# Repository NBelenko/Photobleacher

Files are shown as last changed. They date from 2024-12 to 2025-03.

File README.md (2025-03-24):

# Photobleacher

Photobleacher is an open-source photobleaching device designed to bleach autofluorescence and pigments in biological materials. For more details about the project, please refer to our [publication](https://doi.org/10.1101/2025.02.24.639965).

## About This Repository

This repository contains the following materials.

1. CAD file of the chassis (Enclosure CAD)
2. PCB board design (PCB)
3. Sample stage design (Sample Stage)
4. List of components (Main BOM.xlsx)
5. Wiring diagram (PB Block & Wiring Diagram.pdf)
6. Assembly instructions (PB_Assembly Instructions.pdf)

## Citation

> Murakami et al. Open-source Photobleacher for Fluorescent Imaging of Large Pigment-Rich Tissues. bioRxiv (2025) https://doi.org/10.1101/2025.02.24.639965 

## License

We provide this open source software without any warranty under the [MIT license](https://opensource.org/licenses/MIT).

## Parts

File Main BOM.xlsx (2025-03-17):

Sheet: Enclosure - Digikey
Description | MFGR P/N | Digikey P/N | Qty | Notes
AC/DC CONVERTER 24V 200W | CUS200M-24 | 285-CUS200M-24-ND | 1 | Main PSU
FAN AXIAL 92X20MM 24VDC WIRE | AFB0924HD | 603-1063-ND | 4 | Main Stage Fan
FAN AXIAL 50X20MM 24VDC WIRE | AFB0524VHD | 603-1283-ND | 2 | PSU Fan
PWR ENT MOD RCPT IEC320-C14 PNL | KM01.1205.11 | 486-2280-ND | 1 | PEM (IEC320-C14)
FUSE DRWR FOR PWR MOD F'GRIP 1PL | 4301.1405 | 486-1956-ND | 1 | Fuse drawer for PEM
RELAY GEN PURPOSE DPDT 10A 120V | LY2F-AC110/120 | Z6232-ND | 1 | Power output Relay
FUSE GLASS 2.5A 125VAC 5X20MM | 7010.345 | 486-1837-ND | 1 | Fuse for PEM
CONN RCPT HSG 5POS 3.96MM | VHR-5N | 455-1186-ND | 1 | Input Power connector (AC)
CONN RCPT HSG 6POS 3.96MM | VHR-6N | 455-1187-ND | 1 | Output Power Connector (DC)
CONN SOCKET 18-22AWG CRIMP TIN | SVH-21T-P1.1 | 455-1133-1-ND | 3 | crimp contact for AC input
CONN SOCKET 16-20AWG CRIMP TIN | SVH-41T-P1.1 | 455-1319-1-ND | 6 | crimp contact for DC output
SWITCH ROCKER SPST 16A 125V | KRE2ALA2RBB | CH933-ND | 1 | Front Panel Rocker Switch
CONN QC RCPT 18-22AWG 0.187 | 190030011 | WM18238-ND | Bulk | red QC Female
CONN QC RCPT 14-16AWG 0.187 | 190030056 | WM11242-ND | Bulk | blue QC Female
CONN QC RCPT 18-22AWG 0.187 | 190070010 | WM14190CT-ND | Bulk | red QC Female (flag)
CONN QC RCPT 14-16AWG 0.187 | 190070035 | WM13547-ND | Bulk | blue QC Female (flag)
FILTR ASSB FAN GUARD 92MM 45PPI | 09362-F/45 | CR329-ND | 4 | inlet/Outlet fan cover
FAN GUARD 50MM METAL | 08248 | CR379-ND | 4 | PSU Fan Covers
CONN SPADE TERM 18-22AWG #10 RED | 191420007 | WM13785-ND | Bulk | Spade Power Connector (18-22AWG)
CONN SPADE TERM 14-16AWG #10 BLU | 191310014 | WM13770-ND | Bulk | Spade Power Connector (14-16AWG)
SENSOR REED SW SPST-NO W LEADS | 59150-020 | 59150-020-ND | 1 | Reed Switch for Door
MAGNET 0.375"D X 0.100"THICK CYL | 8008 | 469-1010-ND | 1 | Magnet for Door
HOOK-UP STRND 18AWG BLACK 100' | 891819 BK005 | 891819BK005-ND | 1 | Bulk 18AWG Wire - Black
HOOK-UP STRND 18AWG RED 100' | 891819 RD005 | 891819RD005-ND | 1 | Bulk 18AWG Wire - Red
CONN RING CIRC 14-16AWG #8 CRIMP | 190540110 | WM13634-ND | Bulk | Ring Connector For Terminal Block Bus
Blue Sea Systems DualBus 100A Comon BusBars | 2702 | N/A | 1 | Amazon ASIN: B000277JB4 (Not on Digikey)
SEE PCB Folder For PCB Part BOM

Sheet: Enclosure - McMaster-Carr
Description | McMaster P/N | Qty | Notes
Silicone Sealant Dow Corning 732, 10.1 FL. oz. Cartridge, White | 7587A31 | 1 | Sealant for Spillproofing
Chemical-Resistant Santoprene Sealing Washer (QTY 50) | 94733A411 | 1 | Washers for Stage Spillproofing
Borosilicate Glass Sheet 12" x 8" x 1/4" | 8476K84 | 1 | Glass Sheet for Stage
18-8 Stainless Steel M3 Hex Nuts (QTY 100) | 91828A211 | 1
18-8 Stainless Steel Socket Head Screw M3 x 0.5 mm Thread, 10 mm Long (QTY 100) | 91292A113 | 1 | General purpose mounting screws for LED boards
18-8 Stainless Steel Cup-Point Set Screw M3 x 0.5 mm Thread, 10 mm Long (QTY 50) | 92015A106 | 1 | For Mounting Glass Stage
Female Threaded Hex Standoff 18-8 Stainless Steel, 4.5mm Hex, 10mm Long, M3 x 0.5mm Thread | 94868A006 | 8 | For Mounting Glass Stage
316 Stainless Steel Button Head Hex Drive Screw Super-Corrosion-Resistant, 6-32 Thread Size, 1-1/4" Long (QTY 50) | 98164A444 | 1 | Fan Mounting Hardware
316 Stainless Steel Button Head Hex Drive Screw Super-Corrosion-Resistant, 6-32 Thread Size, 1-1/2" Long (QTY 50) | 98164A445 | 1 | Fan Mounting Hardware
18-8 Stainless Steel Narrow Hex Nut 6-32 Thread Size (QTY 100) | 90730A007 | 1 | Fan Mounting Hardware
High-Temperature Foam Mounting Tape 3M VHB 4611, 1/2" Wide, 15 Feet Long | 7201A21 | 1 | Foam VHB tape for Mounting Parts inside enclosure

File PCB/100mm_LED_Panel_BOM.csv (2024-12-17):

Source: | C:\Users\Griffin\Dropbox (Dropbox @RU)\Precision Instrumentation Technologies\Rockefeller Labs\Heintz Lab (PIT)\Tatz\HEI-2300 Photobleaching Device for Brain Imaging\100mm_LED_Panel\100mm_LED_Panel.kicad_sch
Date: | 1/24/2024 17:04
Tool: | Eeschema (6.0.7)
Generator: | C:\Program Files\KiCad\6.0\bin\scripting\plugins/bom_csv_grouped_by_value.py
Component Count: | 97
Components
Item | Qty | Reference(s) | Value | LibPart | Footprint | Datasheet | DigiKey P/N | Manufacturer | Part Num
1 | 8 | C1-C8 | 0.1u | Device:C_Polarized | Capacitor_Tantalum_SMD:CP_EIA-3216-18_Kemet-A | ~ | 399-3676-1-ND | KEMET | T491A104K035AT
2 | 64 | D1-D64 | LED | Device:LED | Library:LED_Luminus_MP-3030-1100_3.0x3.0mm_Thermal-Vias | ~ | 1214-MP-3030-120H-30-80CT-ND | Luminus Devices Inc. | MP-3030-120H-30-80
3 | 1 | F1 | Polyfuse | Device:Polyfuse | Library:Fuse_2018_5045Metric_Pad_HandSolder | ~ | DECASMDC050F/60-2CT-ND | Littelfuse Inc. | DECASMDC050F/60-2
4 | 4 | J1-J4 | HERM-4-PIN | 100mm_LED_Panel:HERM-4-PIN | Library:TE 2213611-2 4 Position Mini-HERM |  | A124894CT-ND | TE Connectivity AMP Connectors | 2213611-2
5 | 4 | J5-J12 | N/A | Connector_Generic:Conn_01x01 | Library:Faston .25 Tab | ~ | A29938CT-ND | TE Connectivity AMP Connectors | 63824-1
6 | 8 | R1-R8 | 11R | Device:R | Resistor_SMD:R_1206_3216Metric_Pad1.30x1.75mm_HandSolder | ~ | 541-10568-1-ND | Vishay Dale | RCS120611R0FKEA
Collated Components:

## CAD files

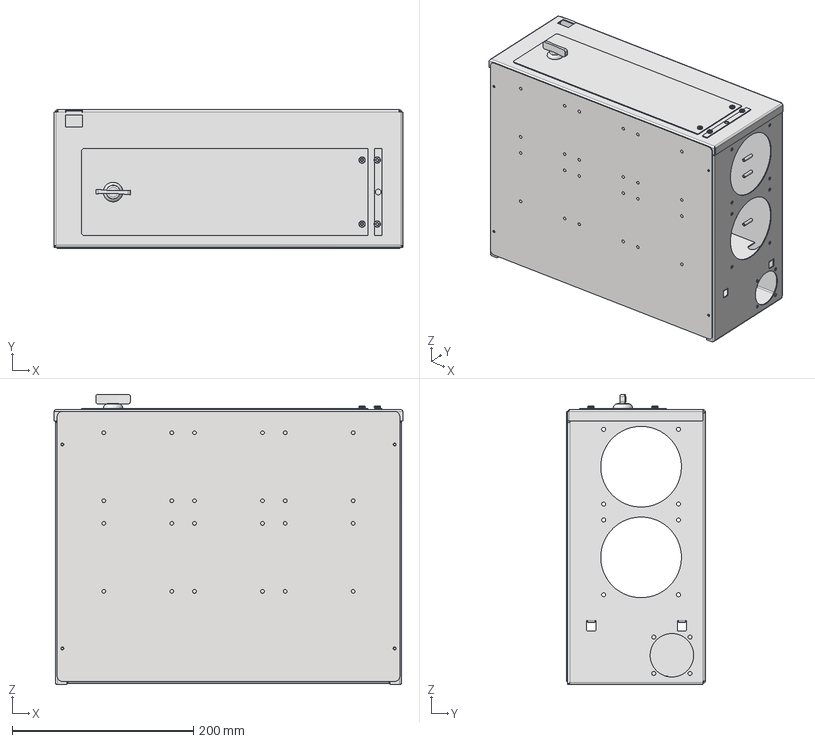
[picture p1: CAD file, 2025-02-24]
Enclosure CAD/RU_Photobleacher_Main_REV_A.stp
385.0 x 153.2 x 320.4 mm
Photobleacher Enclosure Base
Photobleacher Top Cover
Door
Spacer
Bulkhead Plate
1820A21_1820A210-3_8
CLS-M3-1_CLS-M3-1 x 6
BSO-M3-8ZI_BSO-M3-8ZI x 4
BSO-M3-18ZI_BSO-M3-18ZI x 24
BSO-M3-14ZI_BSO-M3-14ZI x 24
S-632-0ZI_S-632-0ZI x 4

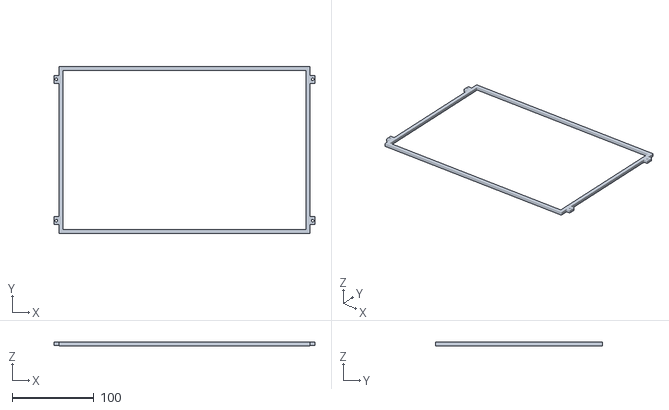
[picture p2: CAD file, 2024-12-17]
Sample Stage/Spill_Tray_bezel.stl
319.6 x 204.6 x 4.50

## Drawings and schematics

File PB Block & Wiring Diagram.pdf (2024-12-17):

## AC Power Input

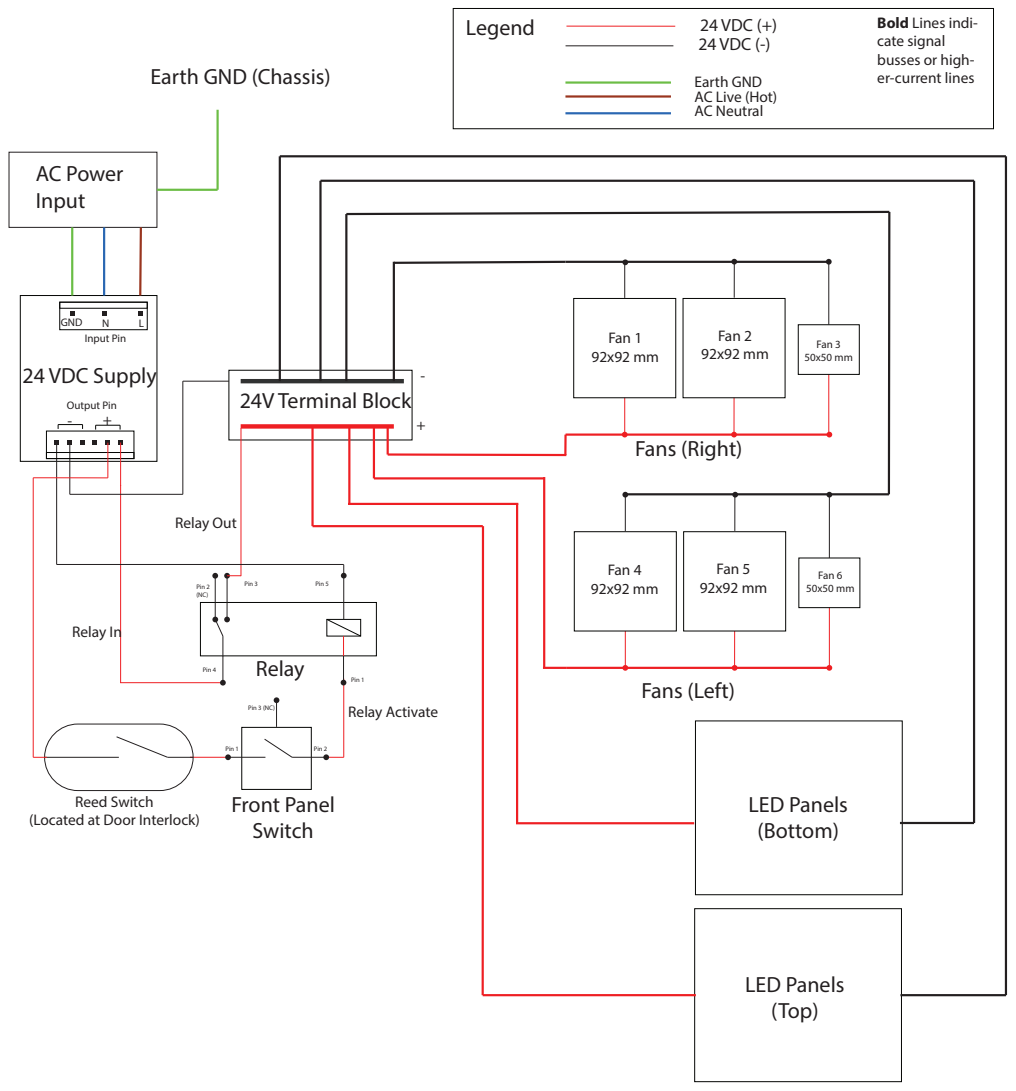
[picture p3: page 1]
24 VDC Supply; Legend; Front Panel Switch; Relay; Relay In; Relay Activate; 24V Terminal Block; Relay Out; Fans (Left); Fans (Right); Fan 4 92x92 mm; LED Panels (Bottom); LED Panels (Top); Pin 1; Pin 2; Pin 3 (NC); Pin 5; Pin 4; Pin 2 (NC); Pin 3; 24 VDC (+) 24 VDC (-); GND; Input Pin; Output Pin; Fan 5 92x92 mm; Fan 6 50x50 mm; Fan 1 92x92 mm; Fan 2 92x92 mm; Fan 3 50x50 mm

Bold Lines indi-
cate signal
busses or high-
er-current lines

Earth GND (Chassis)

Earth GND
AC Live (Hot)
AC Neutral

Reed Switch
(Located at Door Interlock)

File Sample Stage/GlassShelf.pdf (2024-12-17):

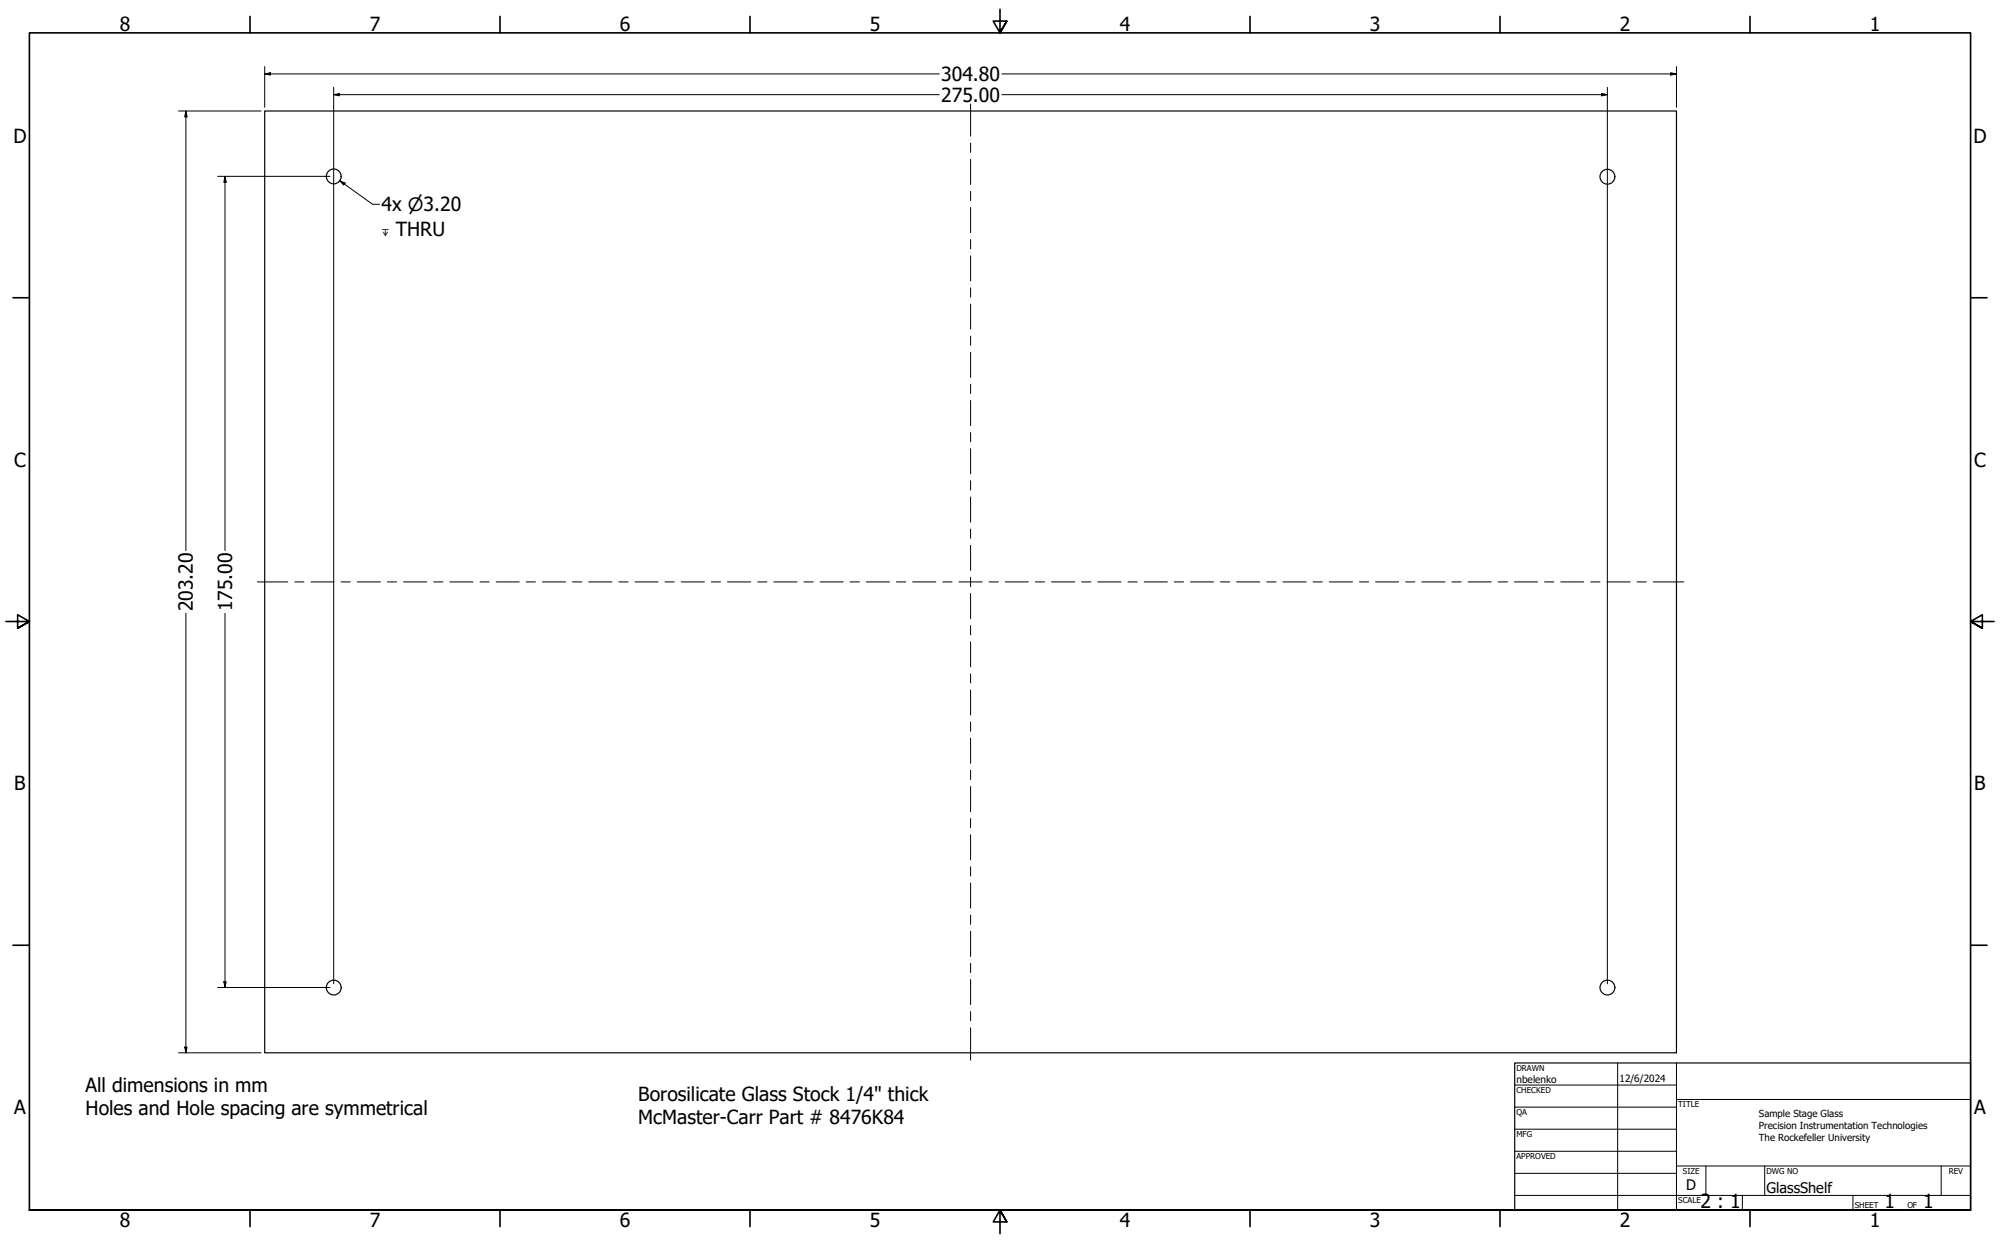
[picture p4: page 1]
↧ THRU

DRAWN nbelenko | 12/6/2024

All dimensions in mm
Holes and Hole spacing are symmetrical

Borosilicate Glass Stock 1/4" thick
McMaster-Carr Part # 8476K84

CHECKED

Sample Stage Glass
Precision Instrumentation Technologies
The Rockefeller University

MFG

APPROVED

SIZE D | DWG NO GlassShelf | REV

2 : 1 SCALE | | SHEET 1 OF 1

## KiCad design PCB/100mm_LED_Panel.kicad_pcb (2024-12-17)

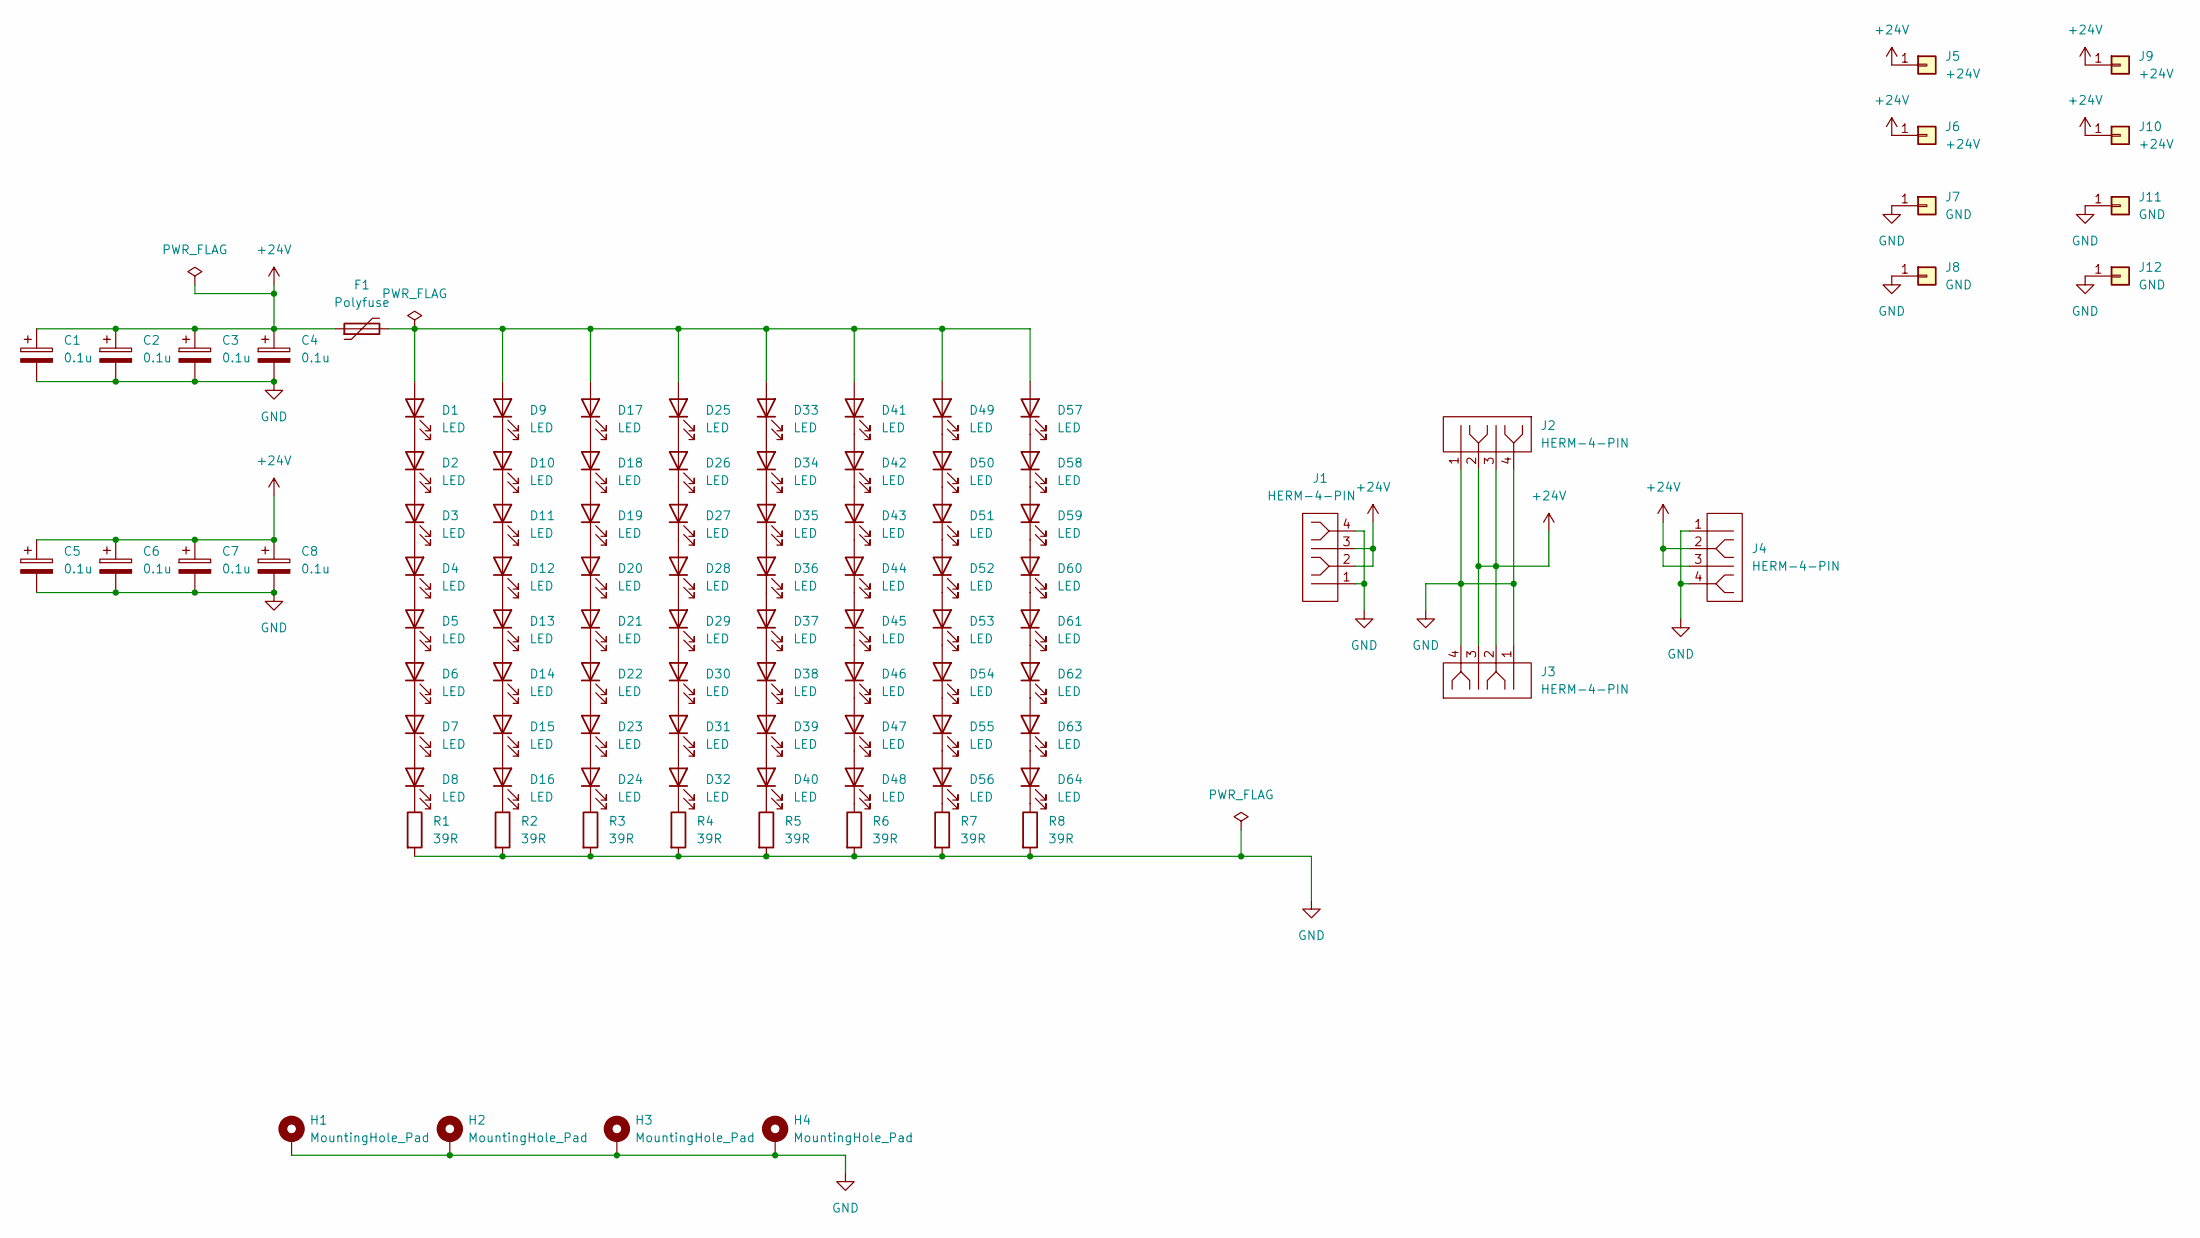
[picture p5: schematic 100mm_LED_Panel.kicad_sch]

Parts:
C1, C2, C3, C4, C5, C6, C7, C8: 0.1u; CP_EIA-3216-18_Kemet-A; Part Num T491A104K035AT; DigiKey P/N 399-3676-1-ND
D1, D2, D3, D4, D5, D6, D7, D8, D9, D10, D11, D12, D13, D14, D15, D16, D17, D18, D19, D20, D21, D22, D23, D24, D25, D26, D27, D28, D29, D30, D31, D32, D33, D34, D35, D36, D37, D38, D39, D40, D41, D42, D43, D44, D45, D46, D47, D48, D49, D50, D51, D52, D53, D54, D55, D56, D57, D58, D59, D60, D61, D62, D63, D64: LED; LED_Luminus_MP-3030-1100_3.0x3.0mm_Thermal-Vias; Part Num MP-3030-120H-30-80; DigiKey P/N 1214-MP-3030-120H-30-80CT-ND
F1: Polyfuse; Fuse_2018_5045Metric_Pad_HandSolder; Part Num DECASMDC050F/60-2; DigiKey P/N DECASMDC050F/60-2CT-ND
H1, H2, H3, H4: MountingHole_Pad; MountingHole_3.2mm_M3_Pad
J1, J2, J3, J4: HERM-4-PIN; TE 2213611-2 4 Position Mini-HERM; Part Num 2213611-2; DigiKey P/N A124894CT-ND
J5, J6, J9, J10: +24V; Faston .25 Tab; Part Num 63824-1; DigiKey P/N A29938CT-ND
J7, J8, J11, J12: GND; Faston .25 Tab; Part Num 63824-1; DigiKey P/N A29938CT-ND
R1, R2, R3, R4, R5, R6, R7, R8: 39R; R_1206_3216Metric_Pad1.30x1.75mm_HandSolder; Part Num RCS120639R0FKEA; DigiKey P/N 541-10632-1-ND

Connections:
+24V: C1.1, C2.1, C3.1, C4.1, C5.1, C6.1, C7.1, C8.1, F1.1, J1.2, J1.3, J2.2, J2.3, J3.2, J3.3, J4.2, J4.3, J5.1, J6.1, J9.1, J10.1
GND: C1.2, C2.2, C3.2, C4.2, C5.2, C6.2, C7.2, C8.2, H1.1, H2.1, H3.1, H4.1, J1.1, J1.4, J2.1, J2.4, J3.1, J3.4, J4.1, J4.4, J7.1, J8.1, J11.1, J12.1, R1.2, R2.2, R3.2, R4.2, R5.2, R6.2, R7.2, R8.2
unnamed: D1.1 (K), D2.2 (A)
unnamed: D1.2 (A), D9.2 (A), D17.2 (A), D25.2 (A), D33.2 (A), D41.2 (A), D49.2 (A), D57.2 (A), F1.2
unnamed: D2.1 (K), D3.2 (A)
unnamed: D3.1 (K), D4.2 (A)
unnamed: D4.1 (K), D5.2 (A)
unnamed: D5.1 (K), D6.2 (A)
unnamed: D6.1 (K), D7.2 (A)
unnamed: D7.1 (K), D8.2 (A)
unnamed: D8.1 (K), R1.1
unnamed: D10.1 (K), D11.2 (A)
unnamed: D9.1 (K), D10.2 (A)
unnamed: D11.1 (K), D12.2 (A)
unnamed: D12.1 (K), D13.2 (A)
unnamed: D13.1 (K), D14.2 (A)
unnamed: D14.1 (K), D15.2 (A)
unnamed: D15.1 (K), D16.2 (A)
unnamed: D16.1 (K), R2.1
unnamed: D17.1 (K), D18.2 (A)
unnamed: D18.1 (K), D19.2 (A)
unnamed: D19.1 (K), D20.2 (A)
unnamed: D20.1 (K), D21.2 (A)
unnamed: D21.1 (K), D22.2 (A)
unnamed: D22.1 (K), D23.2 (A)
unnamed: D23.1 (K), D24.2 (A)
unnamed: D24.1 (K), R3.1
unnamed: D25.1 (K), D26.2 (A)
unnamed: D26.1 (K), D27.2 (A)
unnamed: D27.1 (K), D28.2 (A)
unnamed: D28.1 (K), D29.2 (A)
unnamed: D29.1 (K), D30.2 (A)
unnamed: D30.1 (K), D31.2 (A)
unnamed: D31.1 (K), D32.2 (A)
unnamed: D32.1 (K), R4.1
unnamed: D33.1 (K), D34.2 (A)
unnamed: D34.1 (K), D35.2 (A)
unnamed: D35.1 (K), D36.2 (A)
unnamed: D36.1 (K), D37.2 (A)
unnamed: D37.1 (K), D38.2 (A)
unnamed: D38.1 (K), D39.2 (A)
unnamed: D39.1 (K), D40.2 (A)
unnamed: D40.1 (K), R5.1
unnamed: D41.1 (K), D42.2 (A)
unnamed: D42.1 (K), D43.2 (A)
unnamed: D43.1 (K), D44.2 (A)
unnamed: D44.1 (K), D45.2 (A)
unnamed: D45.1 (K), D46.2 (A)
unnamed: D46.1 (K), D47.2 (A)
unnamed: D47.1 (K), D48.2 (A)
unnamed: D48.1 (K), R6.1
unnamed: D49.1 (K), D50.2 (A)
unnamed: D50.1 (K), D51.2 (A)
unnamed: D51.1 (K), D52.2 (A)
unnamed: D52.1 (K), D53.2 (A)
unnamed: D53.1 (K), D54.2 (A)
unnamed: D54.1 (K), D55.2 (A)
unnamed: D55.1 (K), D56.2 (A)
unnamed: D56.1 (K), R7.1
unnamed: D57.1 (K), D58.2 (A)
unnamed: D58.1 (K), D59.2 (A)
unnamed: D59.1 (K), D60.2 (A)
unnamed: D60.1 (K), D61.2 (A)
unnamed: D61.1 (K), D62.2 (A)
unnamed: D62.1 (K), D63.2 (A)
unnamed: D63.1 (K), D64.2 (A)
unnamed: D64.1 (K), R8.1

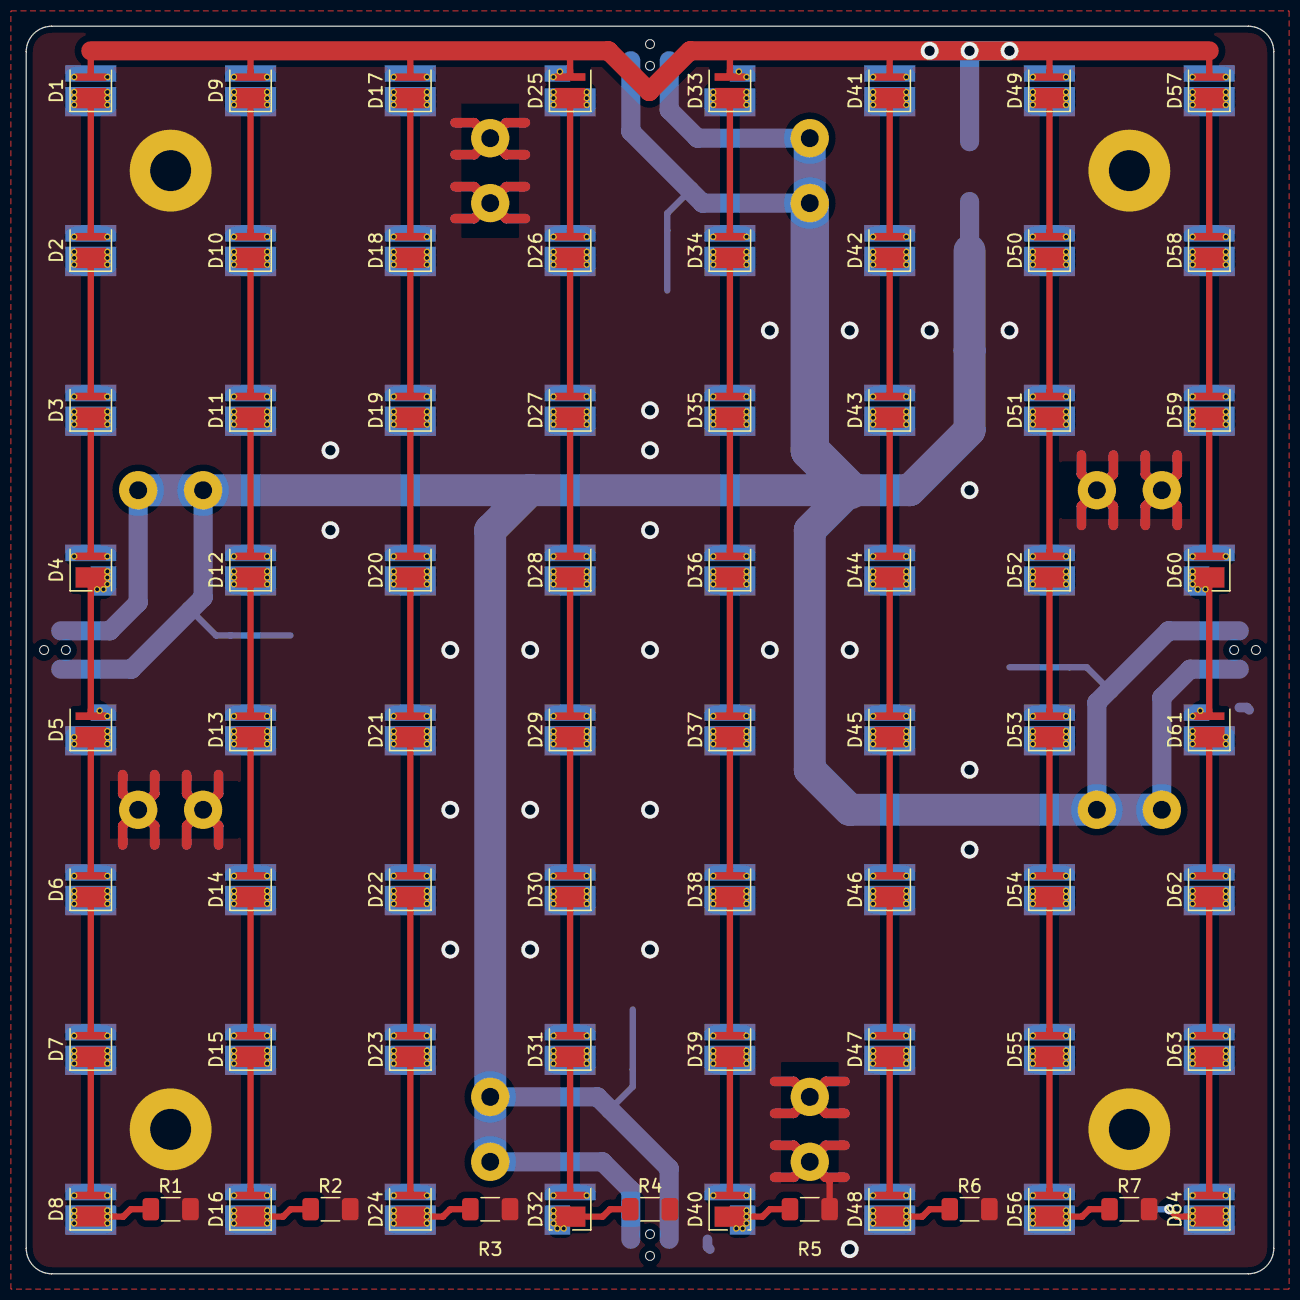
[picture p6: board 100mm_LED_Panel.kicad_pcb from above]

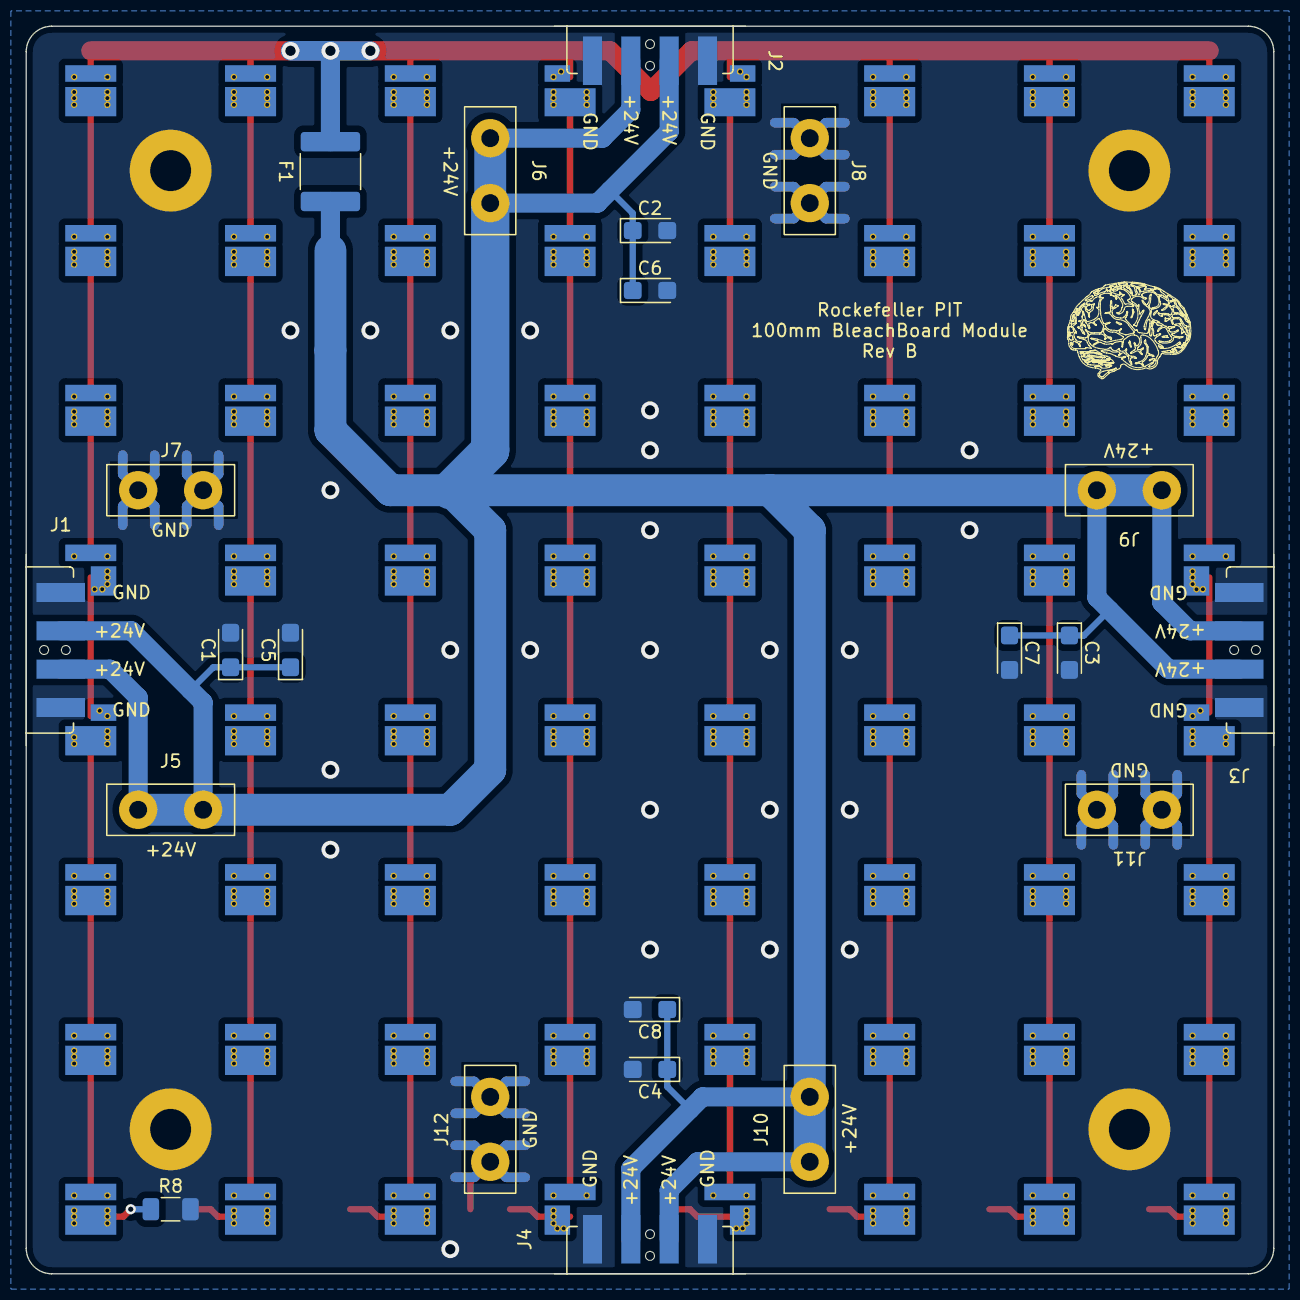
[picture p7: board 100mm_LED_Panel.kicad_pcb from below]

Board: 2 copper layers, 97.6 x 97.6 mm, 97 parts (22 on the bottom side), 67 nets.

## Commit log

2024-12-17 PCB Files
    Board, Schematic, and gerber files for fabrication for the LED panel PCB
2024-12-17 Create stage
2024-12-17 Update and rename 100mm_LED_Panel.csv to 100mm_LED_Panel_BOM.csv
    [100mm_LED_Panel_BOM.csv]
2025-02-24 Added CAD directory/main STEP file
    [RU_Photobleacher_Main_REV_A.stp]
2025-03-17 Main BOM Cleanup
    [Main BOM.xlsx]
